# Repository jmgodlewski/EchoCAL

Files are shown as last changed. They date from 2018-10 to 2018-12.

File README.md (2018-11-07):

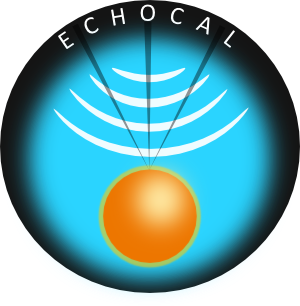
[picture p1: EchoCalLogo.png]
EchoCAL Logo
# EchoCAL: A Wireless Echosounder Calibration System. 

The EchoCAL Wireless Echosounder Calibration System was designed to give Ocean Acoustics researchers the ability to control motorized downriggers remotely during scientific echosounder calibrations. A typical downrigger station consists of a control box wired to a Canon downrigger which is mounted on the railing of the research vessel. A typical calibration on a research vessel requires at least three downrigger stations. (Two on one side of the vessel, and one on the other side.)

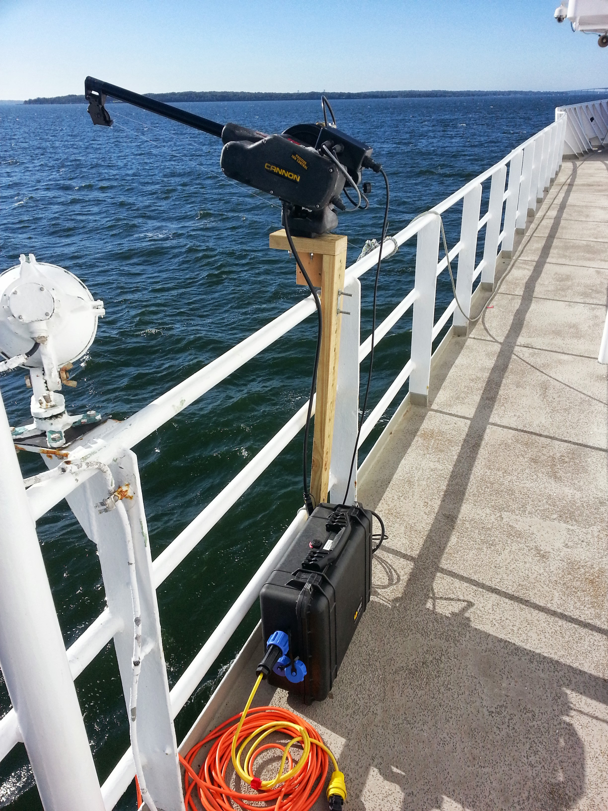
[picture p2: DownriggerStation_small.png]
Smaller Picture of Downrigger Station


The reseacher can control these downriggers wirelessly from inside the vessel. (See the figure below for a system diagram.)

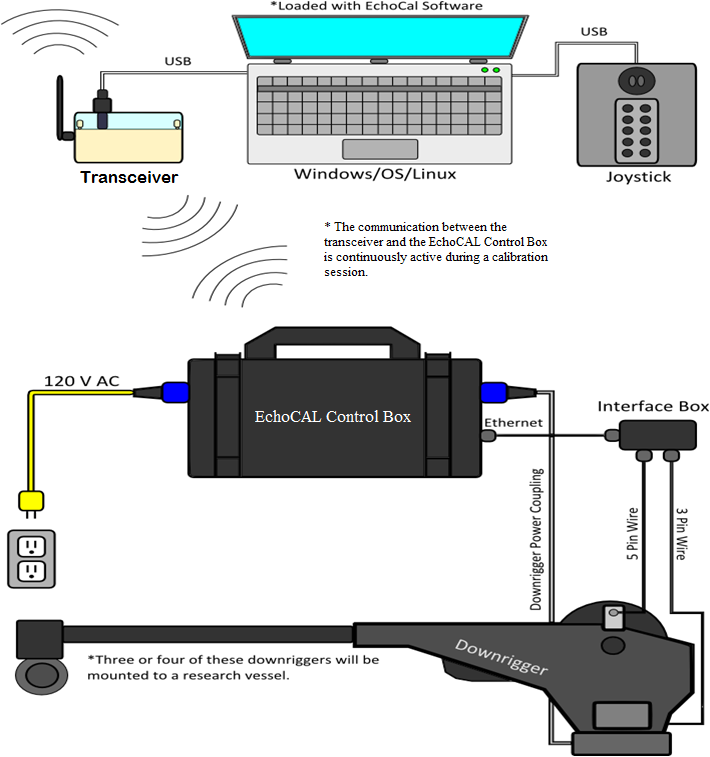
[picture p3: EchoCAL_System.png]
Diagram of EchoCAL System


## EchoCAL Project Files:

The following folders contain the required documentation to build one EchoCAL system:

### DesignFiles:

This folder contains a parts list as well as wiring diagrams for all EchoCAL hardware. This folder has two subfolders, "CircuitCard" and "WiringDiagrams". The "CircuitCard" folder contains the design files to manufacture the EchoCAL custom printed circuitboard (PCB). The "WiringDiagram" folder contains CAD, DXF, and PDF drawings for building all of the hardware for EchoCAL.

### Documentation:

This folder has the Software/Firmware Installation Manuals and the User Manuals.

### EchoCAL_GUI_Source:

This folder contains all of the [Netbeans](https://netbeans.org) JAVA Project source code for the EchoCAL Graphical User Interface (GUI).

### Parallax_Firmware:

This folder contains the firmware for the [Parallax Propeller](https://www.parallax.com/catalog/microcontrollers/propeller) Microcontroller.

### WGFAST_Presentation:

This folder contains a Microsoft PowerPoint presentation of the EchoCAL System. This presentation was given at the Working Group on Fisheries Acoustics, Science, and Technology ([WGFAST](http://www.ices.dk/community/groups/Pages/WGFAST.aspx)) meeting in May 2014. 

### bin:

This folder contains the executable code for the EchoCAL Graphical User Interface (GUI). The JAVA executable code is stored as a ZIP archive that can be downloaded and extracted on a user's computer. The archive was created using Netbeans IDE 8.1 and JAVA JDK 1.8 (64bit).

The "bin" folder has two subfolders, "Win64" and "Linux64". Download the proper version depending on which operating system you will be using.

## Designers:

* **Joseph Godlewski** - *Hardware/Firmware Design* - [jmgodlewski](https://github.com/jmgodlewski)

* **Michael Ryan**     - *EchoCAL GUI Design* - [spacetimeengineer](https://github.com/spacetimeengineer)

## License

EchoCAL is open source! See [LICENSE](./LICENSE.md) for complete license information.

The hardware/software design was written as beerware; if you see us at the local pub, and you've found the hardware and software helpful, please buy us a round!

Please use, reuse, and modify these files as you see fit. Please maintain attribution to NOAA Fisheries, Northeast Fisheries Science Center, and release anything derivative under the same license.

Distributed as-is; no warranty is given.

This project is licensed under the MIT License - see the [LICENSE.md](LICENSE.md) file for details.

## Acknowledgments:

* [Fizzed.com](http://fizzed.com/oss/rxtx-for-java) : Thanks to the developers at Fizzed.com for creating the open source 64-bit modules of the **RXTX** serial communication libraries for JAVA.

* [JInput](https://github.com/jinput/jinput) : Thanks to the developers and maintainers of the open source **JInput** JAVA module for interfacing USB Joystick controllers with Java applications.

* [Parallax Object Exchange](http://obex.parallax.com/) : Thanks to all of the developers who supplied numerous SPIN and Assembly code for the **Parallax Propeller** microcontroller. Their work has made the Propeller microcontroller a joy to work with.

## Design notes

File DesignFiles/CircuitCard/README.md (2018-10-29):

# EchoCAL: Custom Printed Circuit Board (PCB)

The EchoCAL Control Box includes a custom-built printed circuit board "PCB" which incorporates a [Parallax Microcontroller](https://www.parallax.com/product/p8x32a-d40) to interact with Canon Downriggers. This PCB also provides wireless communications with the controlling PC.

These boards can be purchased through [ExpressPCB.com](https://www.expresspcb.com/) using their free schematic and PCB design software.

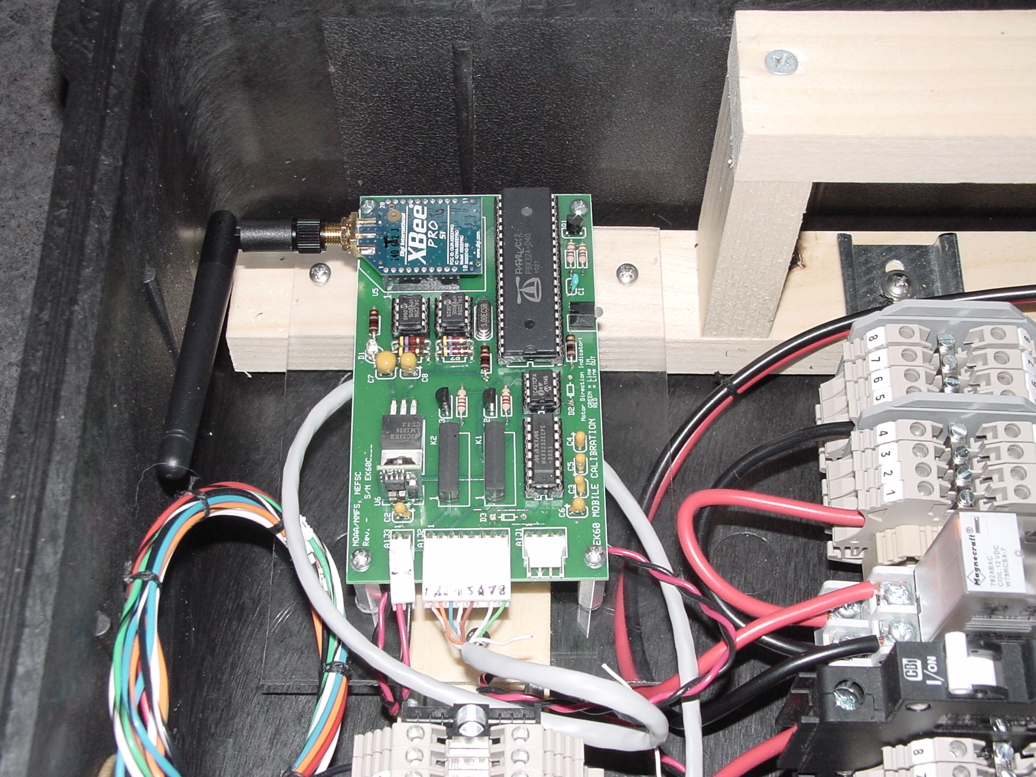
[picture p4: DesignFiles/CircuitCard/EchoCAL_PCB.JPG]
Picture Of PCB


## Purchasing Circuit Boards:

1. Open the "EchoCal_Wireless_RevB.pcb" file using the "expresspcbplus" application.

2. Select the "Order Boards" menu item and choose what type/quantity of boards that you would like. Note: Your PC must be connected to the internet before you can order circuit boards.

### Prerequisites:

The ExpressPCB software runs on Windows PCs only.

## Free Design Software from expresspcb.com

* [ExpressSCH](https://www.expresspcb.com/expresssch/) - Schematic Design software for "EchoCAL_Wireless_RevB.sch" file.
* [ExpressPCB Plus](https://www.expresspcb.com/expresspcbplus/) - PCB Design software for "EchoCAL_Wireless_RevB.pcb" file.

## Designer:

* **Joseph Godlewski** - *Hardware/Firmware Design* - [jmgodlewski](https://github.com/jmgodlewski)

## License

EchoCAL is open source! See [LICENSE](./LICENSE.md) for complete license information.

The hardware/software design was written as beerware; if you see me at the local pub, and you've found the hardware and software helpful, please buy me a round!

Please use, reuse, and modify these files as you see fit. Please maintain attribution to NOAA Fisheries, Northeast Fisheries Science Center, and release anything derivative under the same license.

Distributed as-is; no warranty is given.

This project is licensed under the MIT License - see the [LICENSE.md](LICENSE.md) file for details

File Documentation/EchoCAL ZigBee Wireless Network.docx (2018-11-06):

EchoCAL ZigBee Wireless Network:

Monitoring Network Signal Strength using DigiKey “XCTU” software.

1. A special software package developed by Digi International called “XCTU” is used to monitor the signal strength on the EchoCAL wireless network. This program allows the operator to visually see the signal strengths of all nodes in the ZigBee wireless mesh network.
2. Plug the EchoCAL Base Station into the PCs USB port. Verify which COM port is assigned to this base station using Window’s Device Manager.

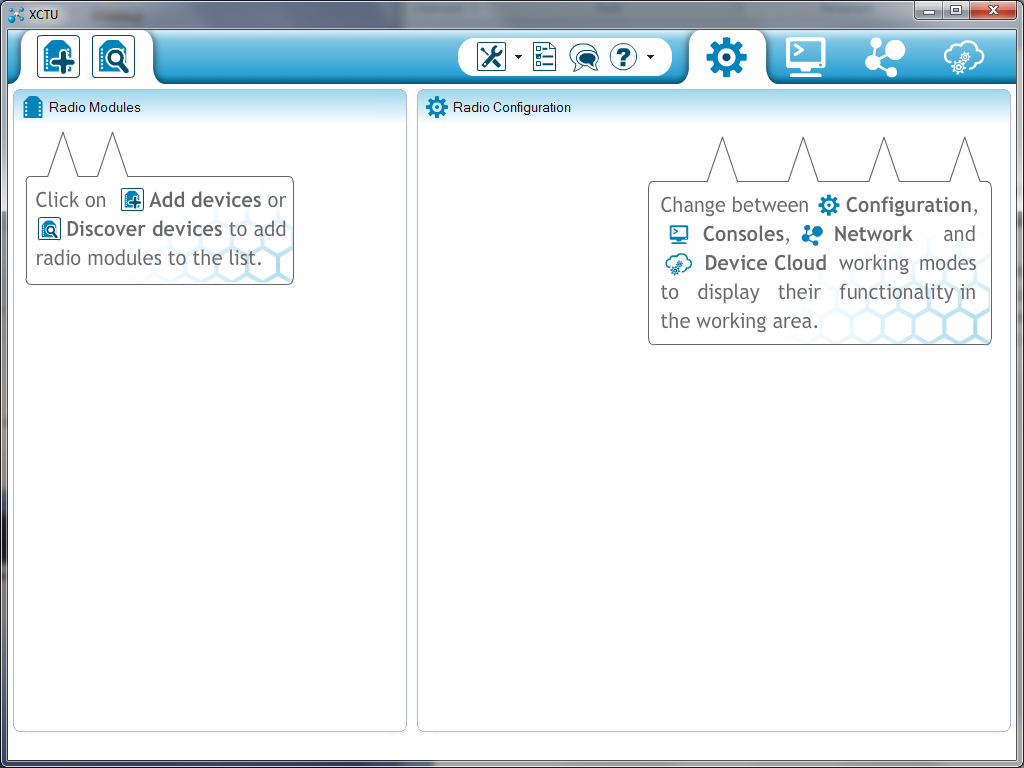
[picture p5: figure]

3. Launch the XCTU software by double-clicking the XCTU icon on the PCs desktop. The XCTU main window will open on the PC.

Discover Devices Tool

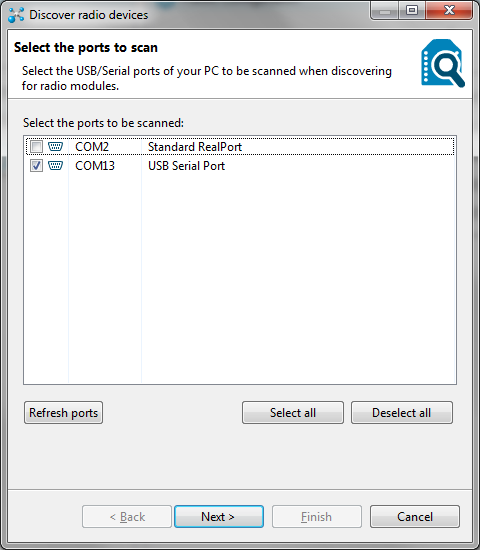
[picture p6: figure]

4. Click on the “Discover devices” tool icon on the top left portion of the XCTU window. This tool allows the software to automatically locate ZigBee transceivers attached to the PC. At this point, the “Discover radio devices” window will open. Select the checkbox next to the COM port that the EchoCAL Base Station is attached to. Click on the “Next” button at the bottom of the window to continue.
5. The “Set port parameters” window will open. Verify that the Serial/USB port parameters are properly configured:
- Baud Rate: 9600,
- Data Bits : 8,
- Parity: None,
- Stop Bits: 1,
- Flow Control: None.

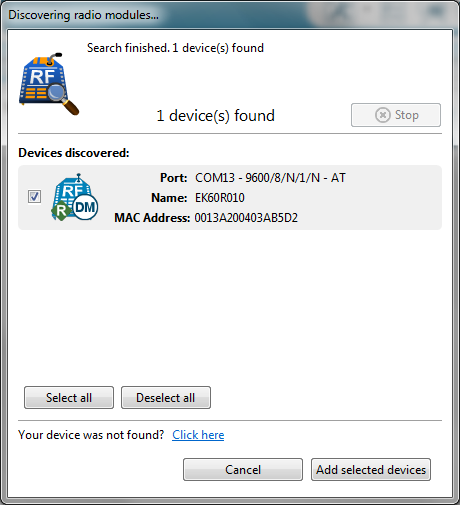
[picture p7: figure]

6. Click on the “Finish” button to continue. A new window will open which will show the device discovered on the PCs COM port. When the device appears on the “Devices discovered” portion of the window, verify that the correct device has been identified. Note: The devices name should be “EK60R010”. Once the device appears, select the “Add selected devices” button to select the base station transceiver.
7. The selected transceiver will appear in the main XCTU window in the left column. Click on this device, and the transceiver’s parameters will begin loading on the right side of window. Using the scroll bar on the right side of the window, scroll down the parameter list until you get to the “Serial Interfacing” portion of the transceiver’s parameter list. Locate the “AP API Enable” parameter under the Serial Interfacing section. In normal EchoCAL operation, this parameter should be set to “Transparent Mode [0]”. Click on this parameter to change the setting to “API without escapes [1]”. This parameter will turn GREEN, indicating that a change was made to this parameter. Click on the red “Pencil” icon to the right of this parameter to save it to the transceiver. Once the “Pencil” icon is selected, the change will be written to the transceiver, and the parameter will turn BLUE in the window. This change needs to be made to allow the transceiver to query other devices on the network about their configuration settings.

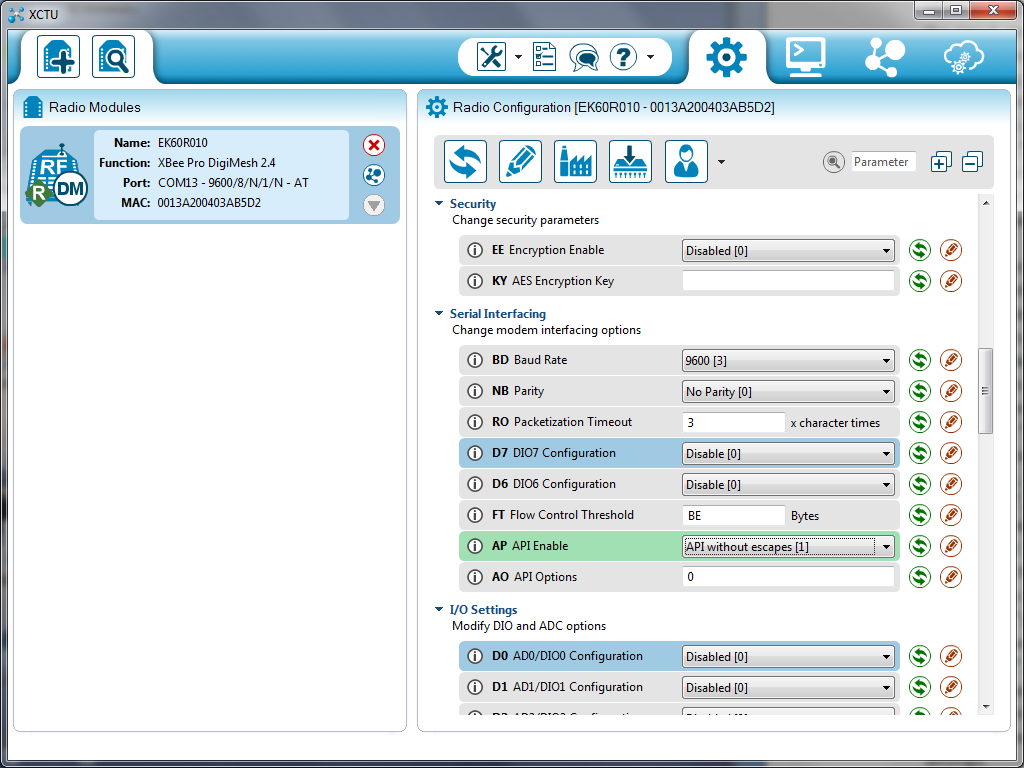
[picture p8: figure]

Discover radio nodes in same network icon:

8. Once the “AP API Enable” parameter has been changed, select the “Discover radio nodes in the same network” icon on the EK60R010 display on the left side of the main program window. This action will launch a new “Discovering remote devices” window, and the software will begin scanning the local wireless network for the various nodes that are available on the mesh network. Make sure all of the installed devices appear on the “New remote devices discovered” portion of this window. When all devices appear in this window, click on the “Add selected devices” button. This window will close, and the selected devices will appear below the base stations entry on the left column in the main XCTU window.

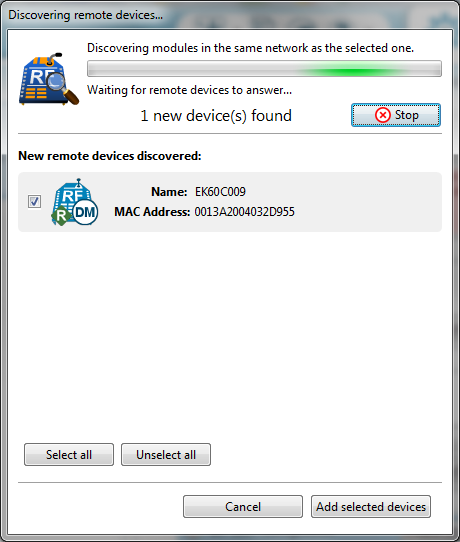
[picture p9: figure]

9. In the main XCTU window, select the “Switch to Networking Mode” tool icon on the right upper tool bar in the main window. The lower right portion will change to a tabbed interface showing the EK60R010 base station in the tab’s label.

Start/Stop scanning the radio module network.

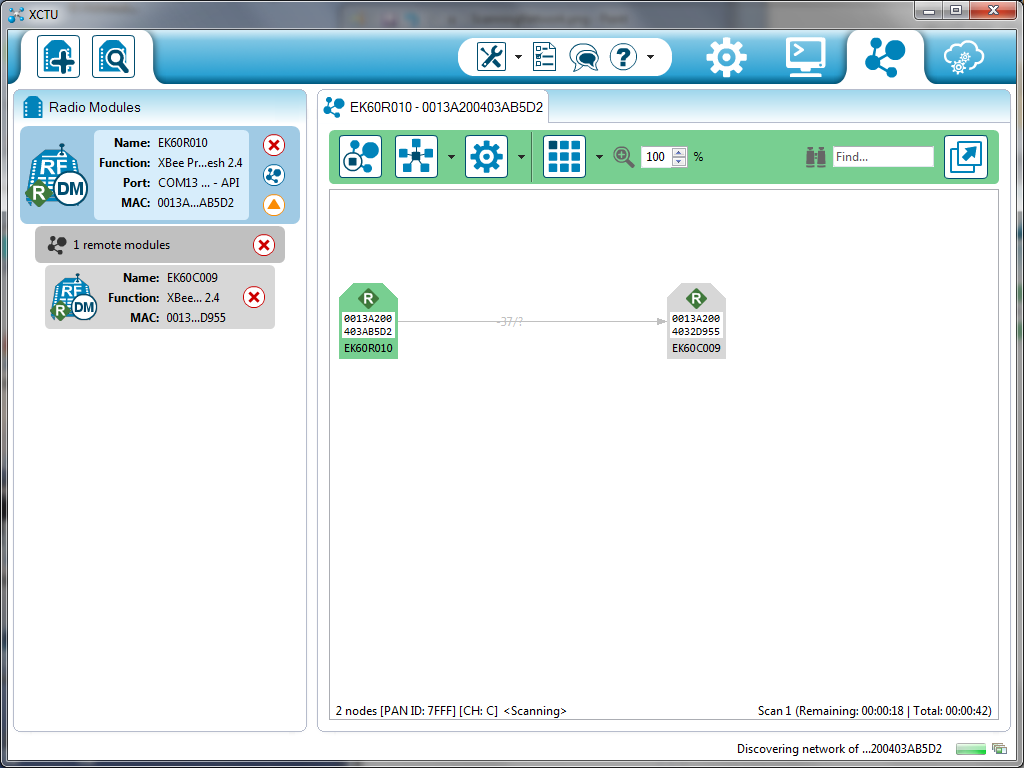
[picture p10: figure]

10. In the tab toolbar portion of the window, select the “Start scanning the radio module network” tool. The lower portion of the tab window will show the EK60R010 graphic which symbolizes the EchoCAL base station. All other transceivers on the network will begin appearing, with links between different transceivers that show the transmit/receive signal power levels. Verify that all of the transceivers appear, and that there is a sufficient transmission path between all transceivers in the network. When satisfied with the performance, select the “Stop scanning the radio module network” tool in the tab’s toolbar.
11. Select the “Switch to Configuration working mode” toolbar in the main window to bring up the parameter settings for the EK60R010 base station.
12. Using the scroll bar on the right side of the window, scroll down the parameter list until you get to the “Serial Interfacing” portion of the transceiver’s parameter list. Locate the “AP API Enable” parameter under the Serial Interfacing section. Click on this parameter to change the setting back to “Transparent Mode [0]”. This parameter will turn GREEN, indicating that a change was made to this parameter. Click on the red “Pencil” icon to the right of this parameter to save it to the transceiver. Once the “Pencil” icon is selected, the change will be written to the transceiver, and the parameter will turn BLUE in the window. This change needs to be made to allow the transceiver to query other devices on the network about their configuration settings.
13. Click on the red X icon on the base station graphic to close the COM port to the base station. Close the XCTU program.

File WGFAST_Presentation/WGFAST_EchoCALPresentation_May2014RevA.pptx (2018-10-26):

## EchoCAL: A mobile wireless calibration system for echo sounders.

Presented By:
Joseph M. Godlewski and Michael Ryan
NOAA,NMFS, NEFSC
Ecosystems Survey Branch
Advanced Sampling Technologies

## EchoCAL: A mobile wireless calibration system for echo sounders

- EchoCAL Hardware:
  - System Diagram;
  - Control Box Assembly;
  - Microcontroller Firmware;
  - Zigbee Wireless Protocol;
    - Wireless Base Station.
    - Wireless Routers.
- EchoCAL Software GUI.
- Results.

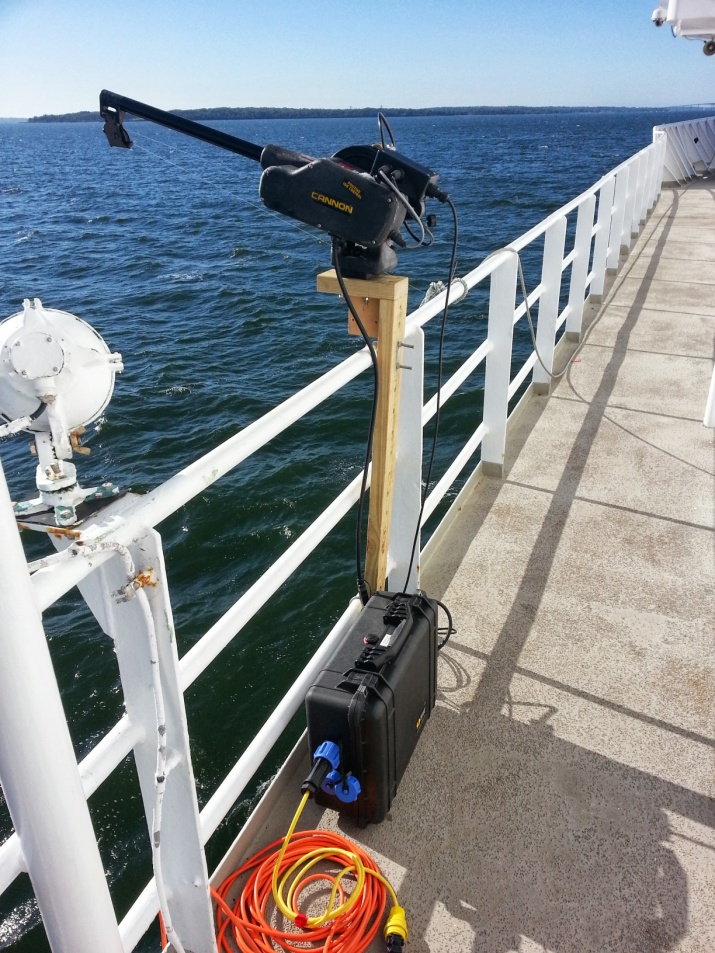
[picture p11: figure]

## EchoCAL System Diagram:

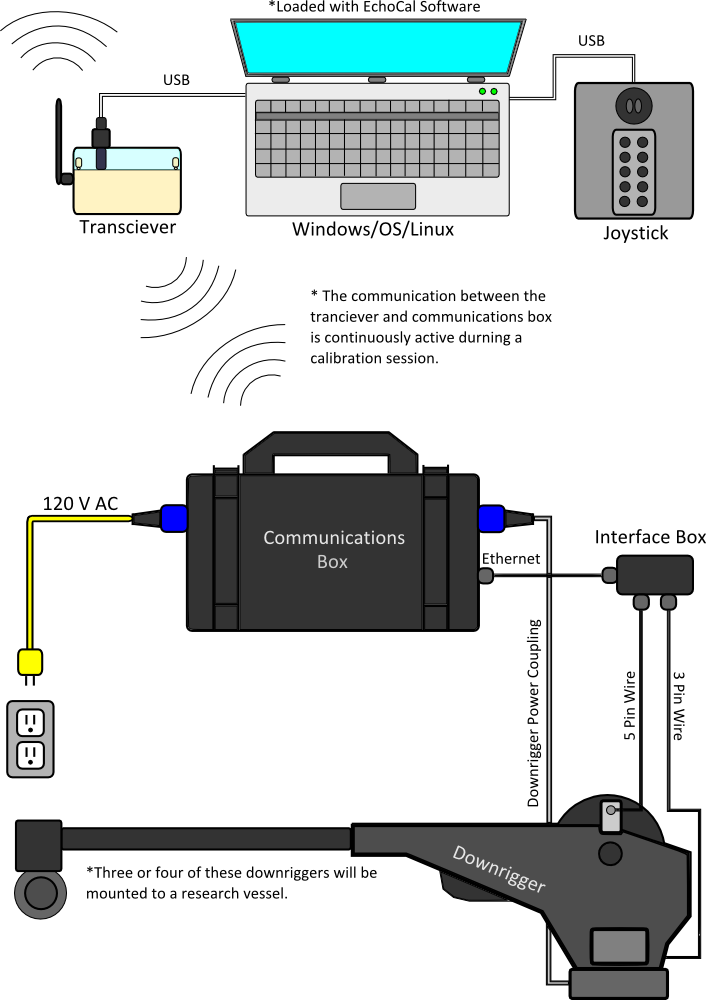
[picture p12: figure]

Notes: Modifications to Cannon Downrigger:

Added connector to downrigger case to wire control box relays in parallel with switch in downrigger.
Mounted 3PS Inc. Quadrature Encoder to outside of downrigger case.
Two magnets installed on downrigger wheel, each mounted at 180 degrees apart.
(This gives us approximately 6 inches of line movement with every “COUNT” of the encoder.)

## EchoCAL Control Box Assembly:

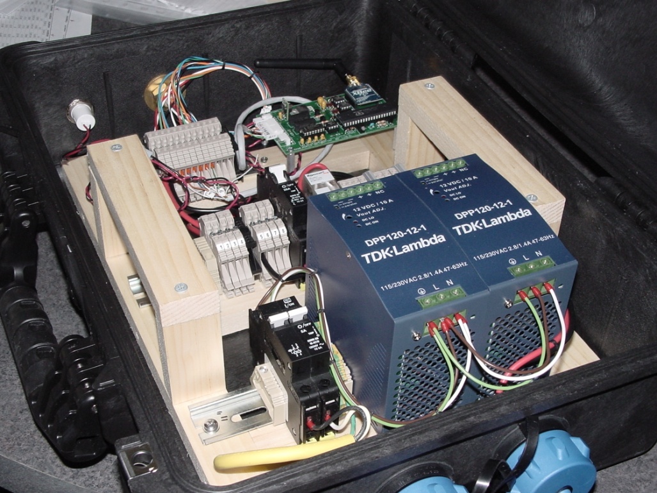
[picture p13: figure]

- Control Box consists of the following components:
  - Two TDK Lambda 12VDC, 10 Amp Power supplies;
  - One TDK Lambda 12VDC, 830 mA Power supply;
  - Custom circuit board with Parallax microcontroller and Digi International XBee Pro Wireless Transceiver;
  - Two power relays for switching between battery and AC power modes.

## Parallax Microcontroller Firmware:

- Parallax Microcontroller programmed using two languages designed specifically for it:
  - “Spin” language = High-level object-based,
  - “Propeller Assembly” = Low-level, highly optimized.
- Microcontroller has eight processing cores (Cogs) which act as a hardware threading mechanism. Allows functions to run in parallel. EchoCAL firmware uses three processing Cogs:
  - One Cog for Main program.
  - Second Cog for handling data and command I/O with XBee Pro transceiver.
  - Third Cog for monitoring the Encoder output and determining direction and line length (ie. Counts) that the downrigger has accomplished.

## XBee Pro Base Station and Router:

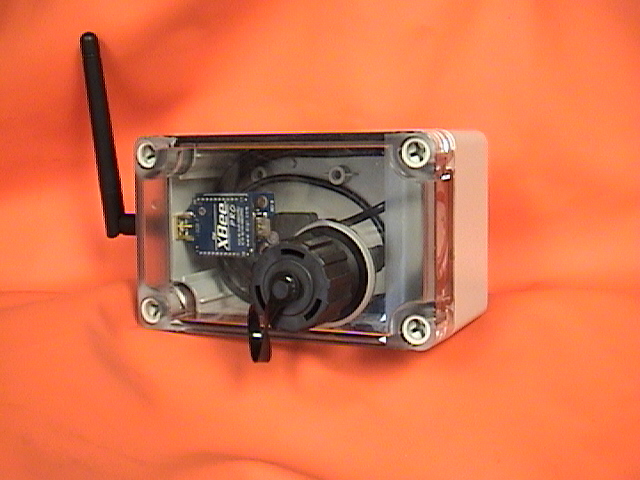
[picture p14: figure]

- The XBee Pro Base Station consists of the following:
  - Parallax XBee USB Adapter board;
  - One Digi Inc. XBee Pro Wireless Transceiver;
  - Power provided by USB bus in the PC.
- The XBee Pro Router hardware:
  - Powered by a 12 VDC, 2000 mAh battery pack.
  - Custom PCB which converts 12 VDC to 3.6 VDC for XBee Pro transceiver operation.

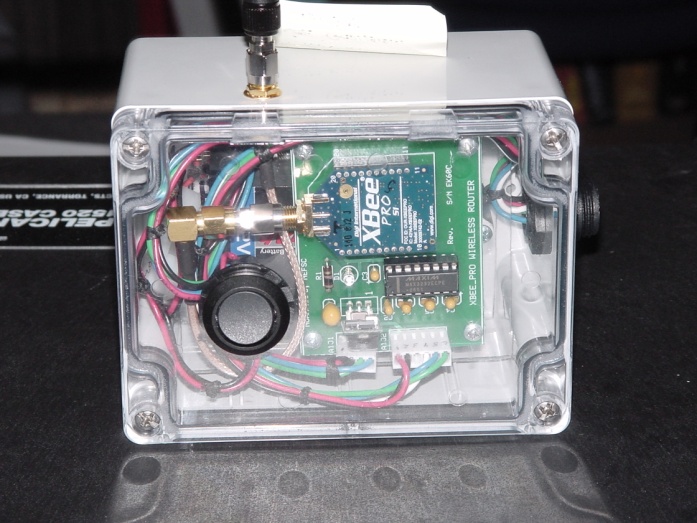
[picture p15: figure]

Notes: XBee Pro Base Station:
- Parallax XBee USB adapter board eliminates the need to build a custom circuit board.
- Simply mount XBee Pro transceiver to adapter board and you are in business.
- Power provided through the USB bus.

XBee Pro Router:
- Powered by a 12 VDC 2000 mAh battery pack.
- Custom circuit board that converts 12 VDC to 3.6 VDC for use with the XBee Pro transceiver.
- Board also contains an Analog Devices ADM3202 RS232 transceiver chip to provide RS232 support for upgrading the XBee Pro transceiver.
- We can do away with the custom PCB if we use the same Parallax XBee USB adapter board that was used in the Base Station.

## XBee Pro Digimesh Network:

- The XBee Pro network is known as a Low Rate Wireless Personal Area Network (LR-WPAN), commonly referred to as a Wireless Sensor Network:
  - Incorporates an Ad Hoc On-Demand Distance Vector mesh routing;
  - Self-healing and discovery capable for network stability;
  - Operates in the 2.4 GHz wireless frequency band;

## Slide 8

EchoCAL Software Interface:

- EchoCAL Software:
  - Developed using JAVA NetBeans IDE platform;
  - Joystick enabled;
  - Location indicators;
  - Programmatic sensors,
  - Hardware safety functions,
  - Automatic navigation function,
  - Navigate function (Sphere locator function).

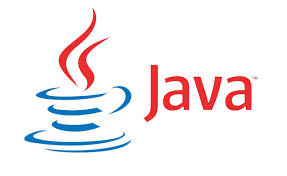
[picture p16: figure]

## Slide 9

EchoCAL Geometry Manager Inputs:
(Visual Reference)

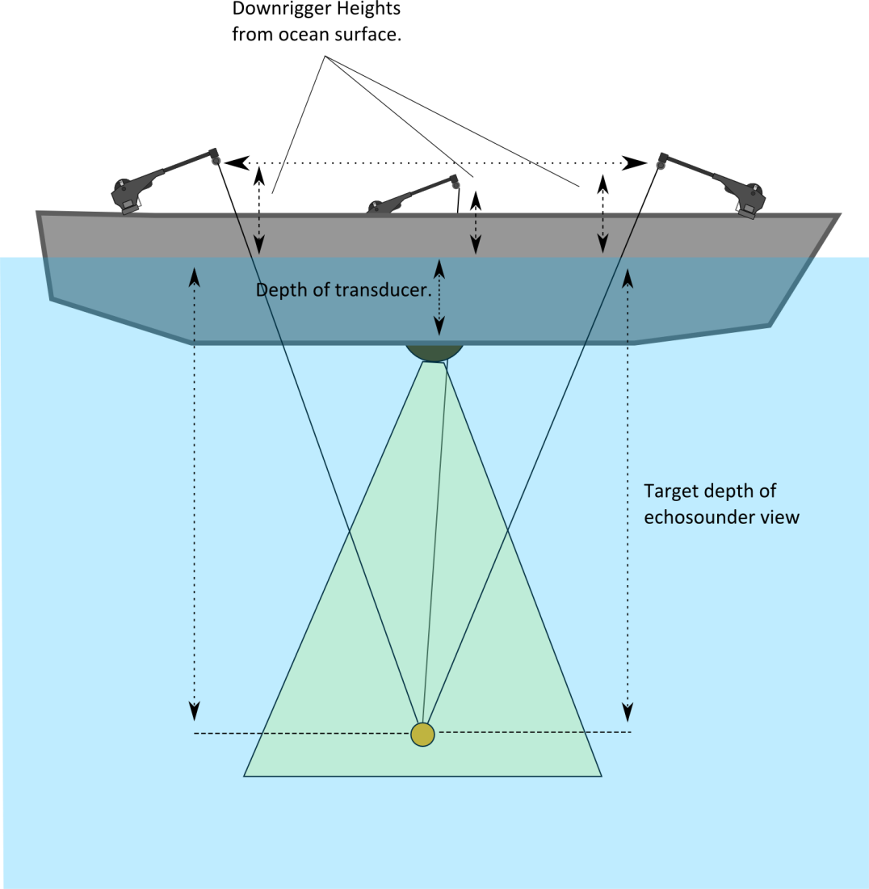
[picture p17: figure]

- Measurements are used to build a geometrical reference map which allows the EchoCAL system to perform accurate automated calibration sessions.

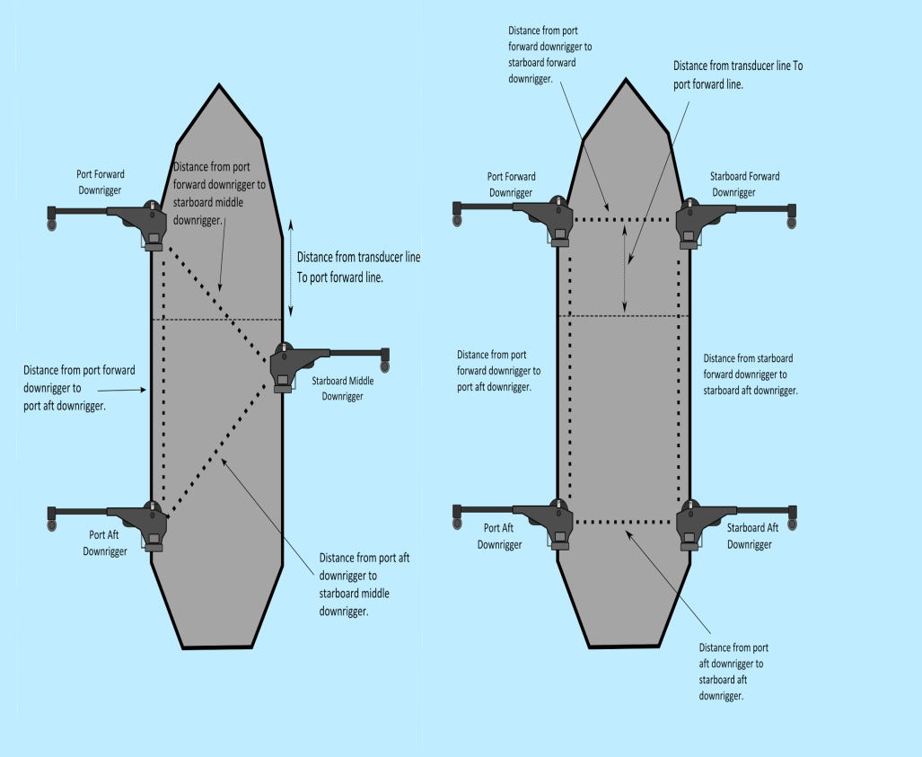
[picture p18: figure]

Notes: Vessel Config file is used to provide a general location of the mounted downriggers on the vessel.
Vessel specific measurements are made to determine the location of the downriggers with respect to the onboard echosounder transducers.

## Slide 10

EchoCAL Graphical User Interface:

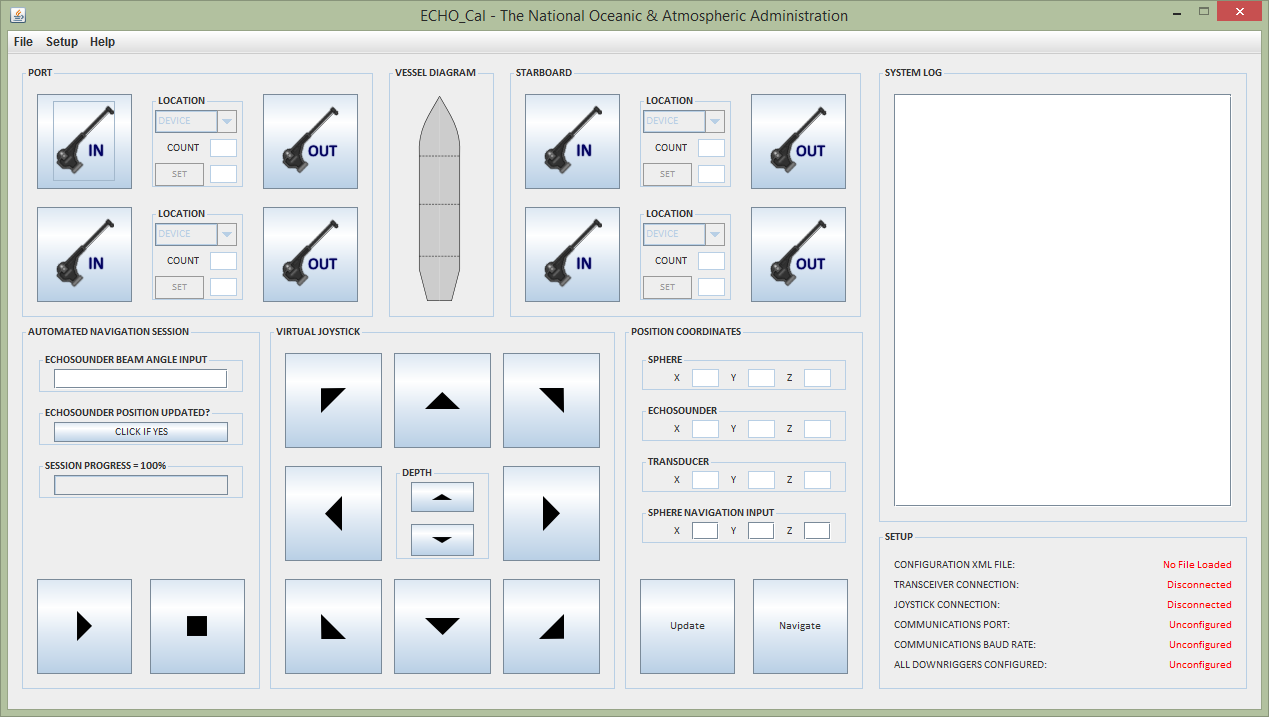
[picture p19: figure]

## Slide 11

EchoCAL’s True Power:
Coordinate Transformation Algorithms

- EchoCAL Software Coordinate Solutions:
  - Uses a process of coordinate filtering to find the Euclidian position of the calibration sphere.
  - Runs on a separate thread so that the geometrical information is updated in real time.
  - Uses the XML configuration file for a geometrical basis.
  - All inputs and outputs are Euclidian, but all calculations are done in downrigger coordinates.

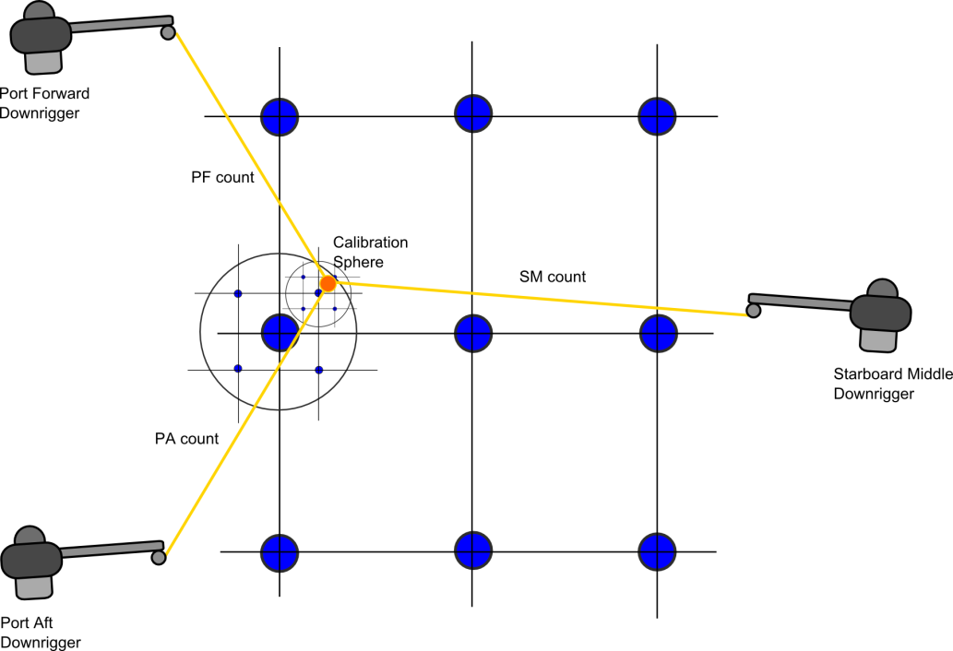
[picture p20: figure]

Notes: Graphic represents a two dimensional view of a three dimensional space.
Each circle represents a set of coordinates. The software checks which downrigger coord transformation is closest to the systems current downrigger counts, and builds another set of points around it. This method builds an array of coordinates

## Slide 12

EchoCAL Automated Calibration Session:

- EchoCALs Automated Navigation Function:
  - Automatically moves the sphere through echosounder beam in a “Star” shaped pattern.
  - Area covered is slightly larger than the beam angle that was input in the GUI.
  - Reasonable coverage is obtained in the echosounder beam.
  - An automated session takes approximately 10 minutes to perform, depending on beam angle size.

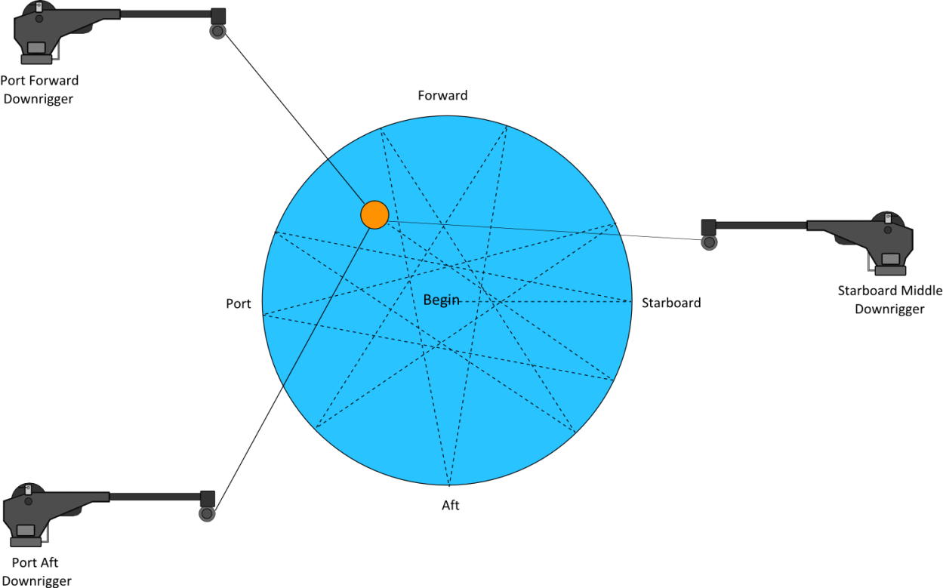
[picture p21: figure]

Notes: EchoCALs Automated Navigation Function:
Automatically moves the sphere through the echosounder beam in a “Star-shaped” pattern.
- Other patterns are being researched.
The area covered is slightly larger than the beam angle that was input in the GUI.
Reasonable coverage is obtained in the echosounder beam.
An automated session takes approximately 10 minutes to perform, depending on the beam angle size.

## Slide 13

EchoCAL Automated Calibration Session:

- EchoCALs Time Saving Abilities:
  - Initially locating the sphere in the echosounder beam can be a difficult task. (Especially when surface winds, or ocean currents are high.) Use of both the “Navigation” and “Auto-navigation” functions allow the operator to easily position the sphere in the echosounder’s beam.
  - Echosounder position updates; (Allows higher order corrections to geometry if system generated values are wrong).
  - Automated calibration sessions: Enjoy a coffee rather than standing out in the rain!

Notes: Time Saving Abilities:
- Initially finding the sphere in the echosounder beam can be a difficult task. (Especially when surface winds, or ocean currents are high.)
The “Navigation” and “Auto-navigation” functions of the EchoCAL software allow the operator to easily position the sphere in the echosounder’s
beam. The Navigation function will get the sphere to the proper depth, and in the vicinity of the echosounder’s beam. If the sphere is not seen
at this point, the operator can perform an initial “Auto-navigation” session with a larger than normal beam angle, and once the sphere appears
in the beam, the operator can stop the “Auto-navigation” session, and position the sphere using the joystick controls.
- Software allows the operator to update the position of the sphere in the center of a beam. This allows operator to reposition the sphere automatically in
the beam should the sphere somehow get lost during calibrations.

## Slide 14

Hardware Safety Functions:

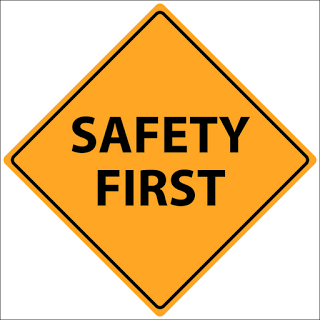
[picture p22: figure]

- EchoCAL Hardware Safety Functions:
  - Built-in tension sensor function to keep lines from breaking.
  - Built-in communication loss warning message.
  - Automatic system halting functions. (Pauses system when mechanical or communication failures occur).
  - Built-In real-time System Log for general information and system status.

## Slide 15

EchoCAL System Results:

- The EchoCAL echosounder calibration system has been used successfully on three NOAA vessels to date:
  - NOAA Ship Okeanos Explorer (April 2013),
  - NOAA Ship Gordon Gunter (April 2014),
  - NOAA Ship Henry Bigelow (September 2013, April 2014).
- Extending the wireless signal outside the vessels proved to be easier than expected. (Only three routers required for the above vessels.)

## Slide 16

EchoCAL System Results:

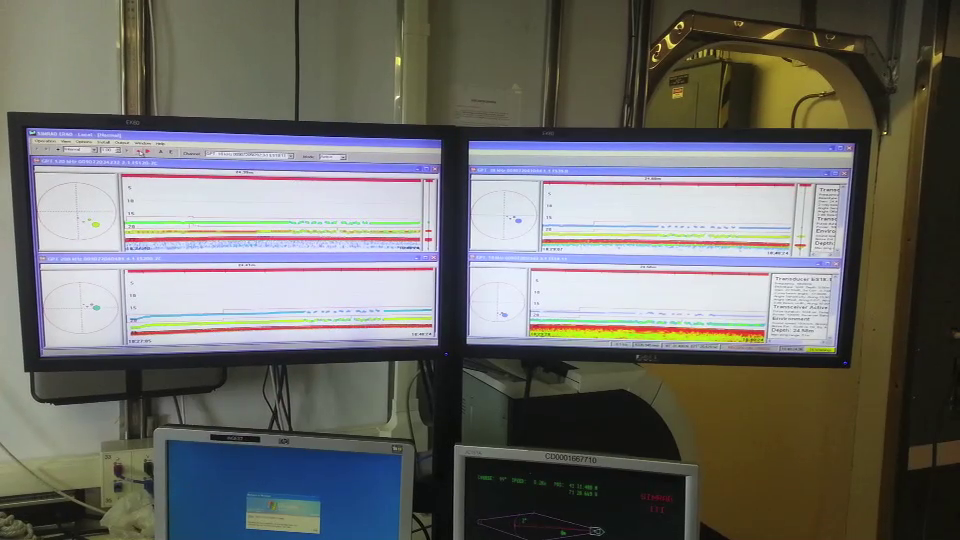
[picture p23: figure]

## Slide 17

EchoCAL System Results:

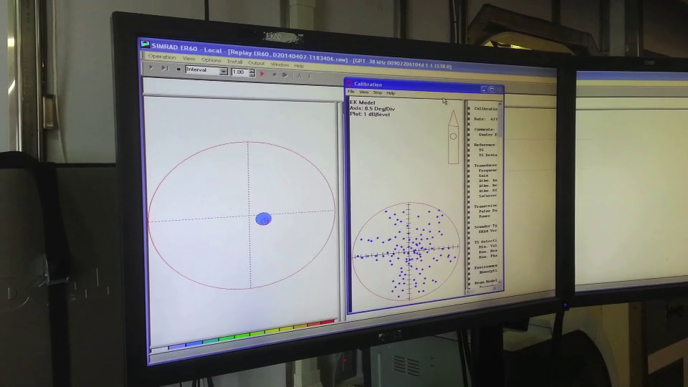
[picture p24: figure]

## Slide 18

- Questions?

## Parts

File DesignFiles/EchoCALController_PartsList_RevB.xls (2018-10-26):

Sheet: EchoCAL Control Box
EchoCAL Wireless Controller: Parts List
Part ID | Part Type | Description | Qty | Cost | Total | Source P/N | Part Source | Notes
EchoCAL Circuit Board A1 Parts:
A1 |  | EchoCAL Circuit Card (PCB) | 1 | $67.28 | $67.28 |  | Express PCB | Production Service (Qty=4) = $269.11.. (Qty = 10, $308.50)
A1J1 |  | Molex P/N 22-05-3041, 4-pin, RA, Friction-Lock Header | 1 | $0.49 | $0.49 | WM4302-ND | Digikey | RS-232 Input Header (4-Pin)
A1J2 |  | Molex P/N 22-05-3081, 8-pin, RA, Friction-Lock Header | 1 | $0.83 | $0.83 | WM4306-ND | Digikey | Downrigger Interface Header (8-Pin)
A1J3 |  | Molex P/N 22-05-3021, 2-pin, RA, Friction-Lock Header | 1 | $0.32 | $0.32 | WM4300-ND | Digikey | Power Input Header (2-Pin)
A1P1 |  | Molex P/N 22-01-3047, 4-socket, Terminal Housing | 1 | $0.19 | $0.19 | WM2002-ND | Digikey | RS-232 Input Connector (4-Socket)
A1P2 |  | Molex P/N 22-01-3087, 8-socket, Terminal Housing | 1 | $0.37 | $0.37 | WM2006-ND | Digikey | Downrigger Interface Connector (8-Socket)
A1P3 |  | Molex P/N 22-01-2027, 2-socket, Terminal Housing | 1 | $0.10 | $0.10 | WM2011-ND | Digikey | Power Input Connector (2-Socket)
 |  | Molex P/N 08-50-0114, Crimp Terminals | 100 | $0.10 | $10.00 | WM1114-ND | Digikey | Crimp sockets for connectors above.
C1 | 0.01uF | Ceramic, +/- 10% | 1 | $0.32 | $0.32 | 490-8813-ND | Digikey
C2 | 1uF | Tantalum, +/- 10% | 1 | $0.65 | $0.65 | 478-1835-ND | Digikey
C3 | 0.1uF | Tantalum, +/- 10% | 1 | $0.66 | $0.66 | 478-1831-ND | Digikey
C4 | 0.1uF | Tantalum, +/- 10% | 1 | $0.46 | $0.46 | 478-1831-ND | Digikey
C5 | 0.1uF | Tantalum, +/- 10% | 1 | $0.46 | $0.46 | 478-1831-ND | Digikey
C6 | 0.1uF | Tantalum, +/- 10% | 1 | $0.46 | $0.46 | 478-1831-ND | Digikey
C7 | 100uF | Tantalum, +/- 10% | 1 | $2.64 | $2.64 | 478-1844-ND | Digikey
C8 | 10uF | Tantalum, +/- 10% | 1 | $0.94 | $0.94 | 478-1841-ND | Digikey
C9 | 1uF | Tantalum, +/- 10% | 1 | $0.65 | $0.65 | 478-1835-ND | Digikey
C10 | 8.2 pF | Ceramic, +/- 5% | 1 | $0.51 | $0.51 | 399-8923-ND | Digikey
D1 |  | Red LED, radial, 3 mm, T-1 | 1 | $0.68 | $0.68 | 511-1190-ND | Digikey
K1 - K2 | W117SIP-6 Relay | Schneider Electric W117SIP-6 Reed Relay, SPST-NO, 5 VDC, 0.5A | 2 | $4.34 | $8.68 | 10M6260 | Newark | www.newark.com (http://www.newark.com/schneider-electric-magnecraft/w117sip-6/relay-reed-spst-no-200v-0-5a-tht/dp/10M6260?ost=10M6260&ddkey=http%3Aen-US%2FElement14_US%2Fsearch)
R1 | 10K | 0.25 W, carbon film resistor, +/- 5% | 1 | $0.10 | $0.10 | 10KQBK-ND | Digikey
R2 | 10K | 0.25 W, carbon film resistor, +/- 5% | 1 | $0.10 | $0.10 | 10KQBK-ND | Digikey
R3 | 10K | 0.25 W, carbon film resistor, +/- 5% | 1 | $0.10 | $0.10 | 10KQBK-ND | Digikey
R4 | 4.7K | 0.25 W, carbon composite resistor, +/- 5% | 1 | $0.10 | $0.10 | CF14JT4K70 | Digikey
R5 | 4.7K | 0.25 W, carbon composite resistor, +/- 5% | 1 | $0.10 | $0.10 | CF14JT4K70 | Digikey
R6 | 4.7K | 0.25 W, carbon composite resistor, +/- 5% | 1 | $0.10 | $0.10 | CF14JT4K70 | Digikey
R7 | 4.7K | 0.25 W, carbon composite resistor, +/- 5% | 1 | $0.10 | $0.10 | CF14JT4K70 | Digikey
R8 | 100 | 0.25 W, carbon composite resistor, +/- 5% | 1 | $0.10 | $0.10 | CF14JT100RCT-ND | Digikey
R9 | 200 | 0.25 W, carbon film resistor, +/- 5% | 1 | $0.10 | $0.10 | 200QBK-ND | Digikey
R10 | 200 | 0.25 W, carbon film resistor, +/- 5% | 1 | $0.10 | $0.10 | 200QBK-ND | Digikey
R11 | 100 | 0.25 W, carbon composite resistor, +/- 5% | 1 | $0.10 | $0.10 | CF14JT100RCT-ND | Digikey
R12 | 20K | 0.25 W, carbon composite resistor, +/- 5% | 1 | $0.10 | $0.10 | 20KQBK-ND | Digikey
R13 | 20K | 0.25 W, carbon composite resistor, +/- 5% | 1 | $0.10 | $0.10 | 20KQBK-ND | Digikey
LT1 |  | Dialight LED Indicator, 3 mm, RED/GREEN, 2.1 Vdc | 1 | $1.76 | $1.76 | 30K1707 | Newark | www.newark.com (http://www.newark.com/dialight/551-3007f/indicator-led-pcb-3mm-red-green/dp/30K1707?ost=30K1707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)
U1 | P8X32A-D40 | Parallax Propeller Microcontroller | 1 | $7.99 | $7.99 | P8X32A-D40-ND | Digikey
U2 | ADM3202ANZ | Analog Divices ADM3202ANZ RS232 Transceiver 460KBPS3.3V DIP16 | 1 | $3.02 | $3.02 | ADM3202ANZ-ND | Digikey
U3 | 24LC256 | 24LC256-E/P 256K EEPROM by MICROCHIP | 1 | $0.91 | $0.91 | 24LC256-E/P-ND | Digikey | I indicates Temp range -45 to 85 C. E = -45 to 125 C.
U4 | 24LC256 | 24LC256-E/P 256K EEPROM by MICROCHIP | 1 | $0.91 | $0.91 | 24LC256-E/P-ND | Digikey | I indicates Temp range -45 to 85 C. E = -45 to 125 C.
U5 | XBee_Pro | Digi Xbee_Pro Wireless Transceiver, XBP9B-DMST-002 | 1 | $39.00 | $39.00 | 602-1299-ND | Digikey | www.digikey.com (https://www.digikey.com/products/en?keywords=602-1299-ND)
 | Antenna | Antenna - 900 MHz, HG, RPSMA Male, articulating | 1 | $7.63 | $7.63 | 553-1474-ND | Digikey | www.digikey.com (https://www.digikey.com/products/en?keywords=553-1474-nd)
U6 | OKI-78SR-5/1.5W36C | Murata OKI-78SR-5 DC to DC Converter, 7.5 W, 5 Vdc output | 1 | $4.30 | $4.30 | 811-2196-5-ND | Digikey
U7 | LM1086IT-3.3/NOPB | LM1086IT-3.3-NOPB by National Semiconductor | 1 | $1.86 | $1.86 | LM1086IT-3.3/NOPB-ND | Digikey
U8 | TC427CPA | Microchip TC427CPA MOSFET Driver, Low Side, 8-pin DIP | 1 | $1.36 | $1.36 | TC427CPA-ND | Digikey | MOSFET Driver
Q1 - Q3 | 2N3904BU | 2N3904 Bipolar Transistor NPN, ON Semiconductor | 3 | $0.21 | $0.63 | 2N3904FS-ND | Digikey
X1 | 5MHz | ECS-50-20-4 5.0 MHz Crystal Oscillator by ECS | 1 | $0.69 | $0.69 | X410-ND | Digikey | This is a 5.0000 MHz crystal
 | A 08-LC-TT | DIP Socket, 8-Pin, AssmanN P/N A08-LC-TT | 3 | $0.18 | $0.54 | AE9986-ND | Digikey
 | A 16-LC-TT | DIP Socket, 16-Pin, AssmanN P/N A16-LC-TT | 1 | $0.25 | $0.25 | AE9992-ND | Digikey
 | A 40-LC-TT | DIP Socket, 40-Pin, AssmanN P/N A40-LC-TT | 1 | $0.51 | $0.51 | AE10008-ND | Digikey
 | SQT-110-01-L-S | SIP Socket, 10-Pin, Samtec P/N SQT-110-01-L-S, 2.00 mm Pitch | 2 | $4.03 | $8.06 | SAM1247-10-ND | Digikey
EchoCAL Control Box Case Parts:
CB1 | C5A2P-489 | American Electrical Circuit Breaker, 240 VAC 5 Amp, 2-pole | 1 | $34.02 | $34.02 | 288-1363-ND | Digikey
CB2 | C20A1P-80VDC | American Electrical Circuit Breaker, 80 VDC 20 Amp, single pole | 1 | $21.06 | $21.06 | 288-1373-ND | Digikey
TB1,2,3 | PEK 2.5 | American Electric Terminal Block, Series PEK 2.5K | 100 | $1.14 | $114.00 | 288-1240-ND | Digikey
 | UK2.5/4 | American Electric Terminal Block Jumpers, 4 Pos. | 15 | $2.39 | $35.85 | 288-1269-ND | Digikey
 | NPP 2.5-10 | American Electric Terminal Block End Plate | 100 | $0.32 | $32.00 | 288-1259-ND | Digikey
 | ASK | American Electric End Bracket | 50 | $0.36 | $18.00 | 288-1295-ND | Digikey
 | 505020 | AE Marking Tags, DY5 | 1 | $1.72 | $1.72 | 288-1296-ND | Digikey
 | 331120 | AE Ground Block, WGT 2.5 | 3 | $3.23 | $9.69 | 288-1248-ND | Digikey
PS1 & 2 | DPP120-12-1 | TDK Lambda 12 VDC Power Supply, 10 Amp | 2 | $80.80 | $161.60 | 285-2032-ND | Digikey
PS3 | DSP10-12 | TDK Lambda 12 VDC Power Supply, 0.830 Amp | 1 | $24.44 | $24.44 | 285-1225-ND | Digikey
K1 | XT484LB2 | Tyco/Schrack Interface Plug-In Relay, 12 VDC coil, 360 ohm | 1 | $8.33 | $8.33 | PB1196-ND | Digikey
 | 6-1415035-1 | Screw terminal, DIN Rail Socket for relay K1 | 1 | $4.95 | $4.95 | PB780-ND | Digikey
K2 | 782XBXC-12D | Magnecraft Power Relay, 12 VDC coil, 20 Amp rated contacts | 1 | $10.54 | $10.54 | 528-7880-7 | Mouser | www.mouser.com
 | 70-459-1 | DIN Rail Socket for relay K2 | 1 | $7.45 | $7.45 | 528-459 | Mouser | www.mouser.com
J1 | PX0931 | Bulgin Bucaneer 900 Series Receptacle, P/N PX0931/03/P | 1 | $23.37 | $23.37 | 708-1205-ND | Digikey | www.digikey.com
P1 | PX0911 | Bulgin Bucaneer 900 Series Plug, P/N PX0911/03/S | 1 | $31.95 | $31.95 | 708-1190-ND | Digikey | www.digikey.com
J2 | PX0931 | Bulgin Bucaneer 900 Series Receptacle, P/N PX0931/02/P | 1 | $19.82 | $19.82 | 708-1204-ND | Digikey | www.digikey.com
P2 | PX0911 | Bulgin Bucaneer 900 Series Plug, P/N PX0911/02/S | 1 | $23.64 | $23.64 | 708-1189-ND | Digikey | www.digikey.com
J3 | PX0931 | Bulgin Bucaneer 900 Series Receptacle, P/N PX0931/02/S | 1 | $21.68 | $21.68 | 708-1209-ND | Digikey | www.digikey.com
P3 | PX0911 | Bulgin Bucaneer 900 Series Plug, P/N PX0911/02/P | 1 | $26.78 | $26.78 | 708-1184-ND | Digikey | www.digikey.com
 | PX0970 | Plastic Cap for J1,J2, & J3 | 3 | $7.94 | $23.82 | 708-1226-ND | Digikey | www.digikey.com
 | 2UB3001-W0000W | Plastic Cap for J1, MultiComp | 1 | $1.97 | $1.97 | 20T7280 | Newark | www.newark.com
J4 | 2TJ3003-W05100 | MultiComp P/N 2TJ3003-W05100, RJ45 Jack, 8 Pos, Panel | 1 | $9.30 | $9.30 | 20T7279 | Newark | www.newark.com
 | 2TJ3000-W05103 | MultiComp Computer Cable, RJ45, 3.5 Meter Length, Black | 1 | $23.77 | $23.77 | 20T7277 | Newark | Use for cable assembly EchoCAL-10520
L1 | 557-1103-203F | Dialight 557 Series Watertight LED Indicator, Red, 12 VDC | 1 | $14.19 | $14.19 | 33M4324 | Newark | www.newark.com
Case | 1520 | Pelican Case, P/N 1520 | 1 | $113.53 | $113.53 |  | Pelican | www.thepelicanstore.com
 | DIN Rail | DIN Rail, 35 x 7.5mm, Slotted 36 inch | 2 | $3.70 | $7.40 | ADR3575-S3600-ND | Digikey | www.digikey.com
 |  |  | TOTAL: |  | $1002.28
 |  | Control Box Total: | $1002.28
 |  | XBeePro Router Total: | $167.24 | Price is for one router. You probably need about three routers to get wireless signal outside research vessel.
 |  | Downrigger Interface Box Total: | $83.65
 |  | Wireless Base Station: | $126.81
 |  | 3PS Inc. Hall Effect Sensor P/N QUAD101-01-01-01-0 | $850.80 | Need to reconsider use of this sensor. Price has almost tripled in the past 5 years.
 |  | Cannon Magnum 5ST Downrigger: | $429.99
 |  | Total System Cost per unit: | $2660.77

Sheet: XBeePro Router
XBee_Pro Wireless Router: Parts List
Part ID | Part Type | Description | Qty | Cost | Total | Source P/N | Part Source | Notes
XBee_Pro Router Circuit Board A1 Parts:
A1 |  | Sparkfun XBee Explorer, P/N WRL-11373 | 1 | $9.95 | $9.95 | WRL-11373 | Sparkfun | Sparkfun.com (https://www.sparkfun.com/products/11373)
A1J1 |  | Molex P/N 22-05-3081, 6-pin, RA, Friction-Lock Header | 1 | $0.65 | $0.65 | WM4304-ND | Digikey | Power/XBee Interface Right Angle Header (6-Pin)
A1P1 |  | Molex P/N 22-01-2067, 6-socket, Terminal Housing | 1 | $0.26 | $0.26 | WM2015-ND | Digikey | Power/XBee Interface Connector (6-Socket)
 |  | Molex P/N 08-50-0114, Crimp Terminals | 100 | $0.10 | $10.00 | WM1114-ND | Digikey | Crimp sockets for connectors above.
U3 | XBee_Pro | Digi Xbee_Pro Wireless Transceiver, XBP9B-DMST-002 | 1 | $39.00 | $39.00 | 602-1299-ND | Digikey | www.digikey.com (https://www.digikey.com/products/en?keywords=602-1299-nd)
 | Antenna, 900 MHz | Antenna - 900 MHz, Half Wave Dipole, 2.1 dBi, RPSMA Male, articulating | 1 | $7.63 | $7.63 | 553-1474-ND | Digikey | www.digikey.com (https://www.digikey.com/products/en?keywords=553-1474-nd)
XBee Router Case Parts:
B1 | 4.8 VDC Battery | Tenergy 4.8 V 2000 mAh NiMH Battery Pack | 1 | $12.99 | $12.99 | 11001 | All-Battery.com | www.all-battery.com (http://www.all-battery.com/48v2000mahnimhreceiverrxbattery11001.aspx)
S1 | Power Switch | E-Switch P/N RR313BBLKBLKES, Rocker Switch | 1 | $3.45 | $3.45 | 612-RR3130B | Mouser | www.mouser.com
 | 1554G2GYCL | Hammond Enclosure, polycarbonate, clear cover 4.72H x 3.54W x 3.14D | 1 | $19.77 | $19.77 | 98H1120 | Newark | www.newark.com (http://www.newark.com/hammond/1554g2gycl/enclosure-din-rail-polycarbonate/dp/98H1120?ost=98h1120&ddkey=http%3Aen-US%2FElement14_US%2Fsearch)
BTJ1 |  | Molex Receptacle P/N 03-06-1042-S, 4 POS | 1 | $0.15 | $0.15 | 38C8696 | Newark | www.newark.com
BTP1 |  | Molex Plug P/N 03-06-2042-P, 4 POS | 1 | $0.38 | $0.38 | 38C8709 | Newark | www.newark.com
BTJ2&3 |  | Molex Receptacle P/N 03-06-1023-S, 2 POS | 2 | $0.20 | $0.40 | 26C1314 | Newark | www.newark.com
BTJ2&3 |  | Molex Plug P/N 03-06-2023-P, 2 POS | 2 | $0.20 | $0.40 | 26C1313 | Newark | www.newark.com
 |  | Crimp sockets for BTJ1, Molex P/N 02-06-1132 | 100 | $0.06 | $6.00 | 85C0027 | Newark | www.newark.com
 |  | Crimp pins for BTP1, Molex P/N 02-06-2132 | 100 | $0.09 | $9.00 | 85C0026 | Newark | www.newark.com
J1 |  | Bulgin Buccaneer receptacle, P/N PX0412/06/S/4550, 6 sockets | 1 | $8.11 | $8.11 | 92C2468 | Newark | www.newark.com
P1 |  | Bulgin Buccaneer plug, P/N PX0410/06/P/4550, 6 pins | 1 | $9.51 | $9.51 | 92C2439 | Newark | www.newark.com
 |  | Sealing cap for P1, Bulgin P/N PX0481 | 1 | $2.51 | $2.51 | 92C2477 | Newark | www.newark.com
 |  | Sealing cap for J1, Bulgin P/N PX0480 | 1 | $2.46 | $2.46 | 92C2475 | Newark | www.newark.com
 |  | Solder Contacts for P1, P/N SA3348/1, Pack of 10 | 1 | $9.50 | $9.50 | 92C3200 | Newark | www.newark.com
 |  | Solder Contacts for S1, P/N SA3347/1, Pack of 10 | 1 | $15.12 | $15.12 | 92C3198 | Newark | www.newark.com
 |  |  | TOTAL: |  | $167.24

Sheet: DownriggerInterfaceBox
Downrigger Interface Box: Parts List
Part ID | Part Type | Description | Qty | Cost | Total | Source P/N | Part Source | Notes
 | 2UB3001-W0000W | Plastic Cap for J1, MultiComp | 1 | $1.97 | $1.97 | 20T7280 | Newark | www.newark.com
J1 | 2TJ3003-W05100 | MultiComp P/N 2TJ3003-W05100, RJ45 Jack, 8 Pos, Panel | 1 | $9.30 | $9.30 | 20T7279 | Newark | www.newark.com
J2 | EN3P5FX | Switchcraft Receptacle, 5 position Female, P/N EN3P5FX | 1 | $9.46 | $9.46 | SC264-ND | Digikey | www.digikey.com
J3 | EN3P3FX | Switchcraft Receptacle, 3 position Female, P/N EN3P3FX | 2 | $7.06 | $14.12 | SC260-ND | Digikey | www.digikey.com
P3 | EN3C3MX | Switchcraft Plug, 3 position Male, P/N EN3C3MX | 2 | $5.79 | $11.58 | SC252-ND | Digikey | www.digikey.com
P2 | EN3C5MX | Switchcraft Plug, 5 position Male, P/N EN3C5MX | 1 | $6.35 | $6.35 | SC256-ND | Digikey | www.digikey.com
 | EN3CAP | Switchcraft Weatherproof Caps for J2, J3, P2, and P3 | 6 | $1.85 | $11.10 | SC1174-ND | Digikey | www.digikey.com
 | 1554G2GYCL | Hammond P/N 1554G2GYCL Enclosure | 1 | $19.77 | $19.77 | 98H1120 | Newark | www.newark.com (http://www.newark.com/hammond/1554g2gycl/enclosure-din-rail-polycarbonate/dp/98H1120?ost=98h1120&ddkey=http%3Aen-US%2FElement14_US%2Fsearch)
 |  |  | TOTAL: |  | $83.65

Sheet: BaseStation
Wireless Base Station: Parts List
Part ID | Part Type | Description | Qty | Cost | Total | Source P/N | Part Source | Notes
J1 | 17-200161 | CONEC IP67 USB Connector, USB Female Adapter | 1 | $13.16 | $13.16 | 706-17-200161 | Mouser | www.mouser.com
 | 17-200231 | USB Patch Cord, 2 meters (for use with J1) | 1 | $13.99 | $13.99 | 706-17-200231 | Mouser | www.mouser.com (https://www.mouser.com/ProductDetail/CONEC/17-200231)
 | CSMUAMB5-03M | USB Cable Type A to Mini-B 5 Position, 0.3 meters | 1 | $8.27 | $8.27 | CSMUAMB5-03M | L-Com | www.l-com.com (http://www.l-com.com/usb-premium-usb-cable-type-a-mini-b-5-position-03m)
1A1 | 32400 | Parallax XBee USB Adapter Board | 1 | $24.99 | $24.99 | 32400 | Parallax | www.parallax.com (https://www.parallax.com/product/32400)
U1 | XBee_Pro | Digi Xbee_Pro Wireless Transceiver, XBP9B-DMST-002 | 1 | $39.00 | $39.00 | 602-1299-ND | Digikey | www.digikey.com (https://www.digikey.com/products/en?keywords=602-1299-nd)
 | Antenna,900 MHz | Antenna - 900 MHz, Half Wave Dipole, 2.1 dBi, RPSMA Male, articulating | 1 | $7.63 | $7.63 | 553-1474-ND | Digikey | www.digikey.com (https://www.digikey.com/products/en?keywords=553-1474-nd)
 | 1554G2GYCL | Hammond Enclosure, polycarbonate, clear cover 4.72H x 3.54W x 3.14D | 1 | $19.77 | $19.77 | 98H1120 | Newark | www.newark.com (http://www.newark.com/hammond/1554g2gycl/enclosure-din-rail-polycarbonate/dp/98H1120?ost=98h1120&ddkey=http%3Aen-US%2FElement14_US%2Fsearch)
 | PN-1328-CMB | BUD Enclosure, Polycarbonate with clear cover, 4.53H x 3.54W x 3.15D | 0 | $14.50 | $0.00 | 40T8055 | Newark | (optional enclosure) (http://www.newark.com/)
 |  |  | TOTAL: |  | $126.81

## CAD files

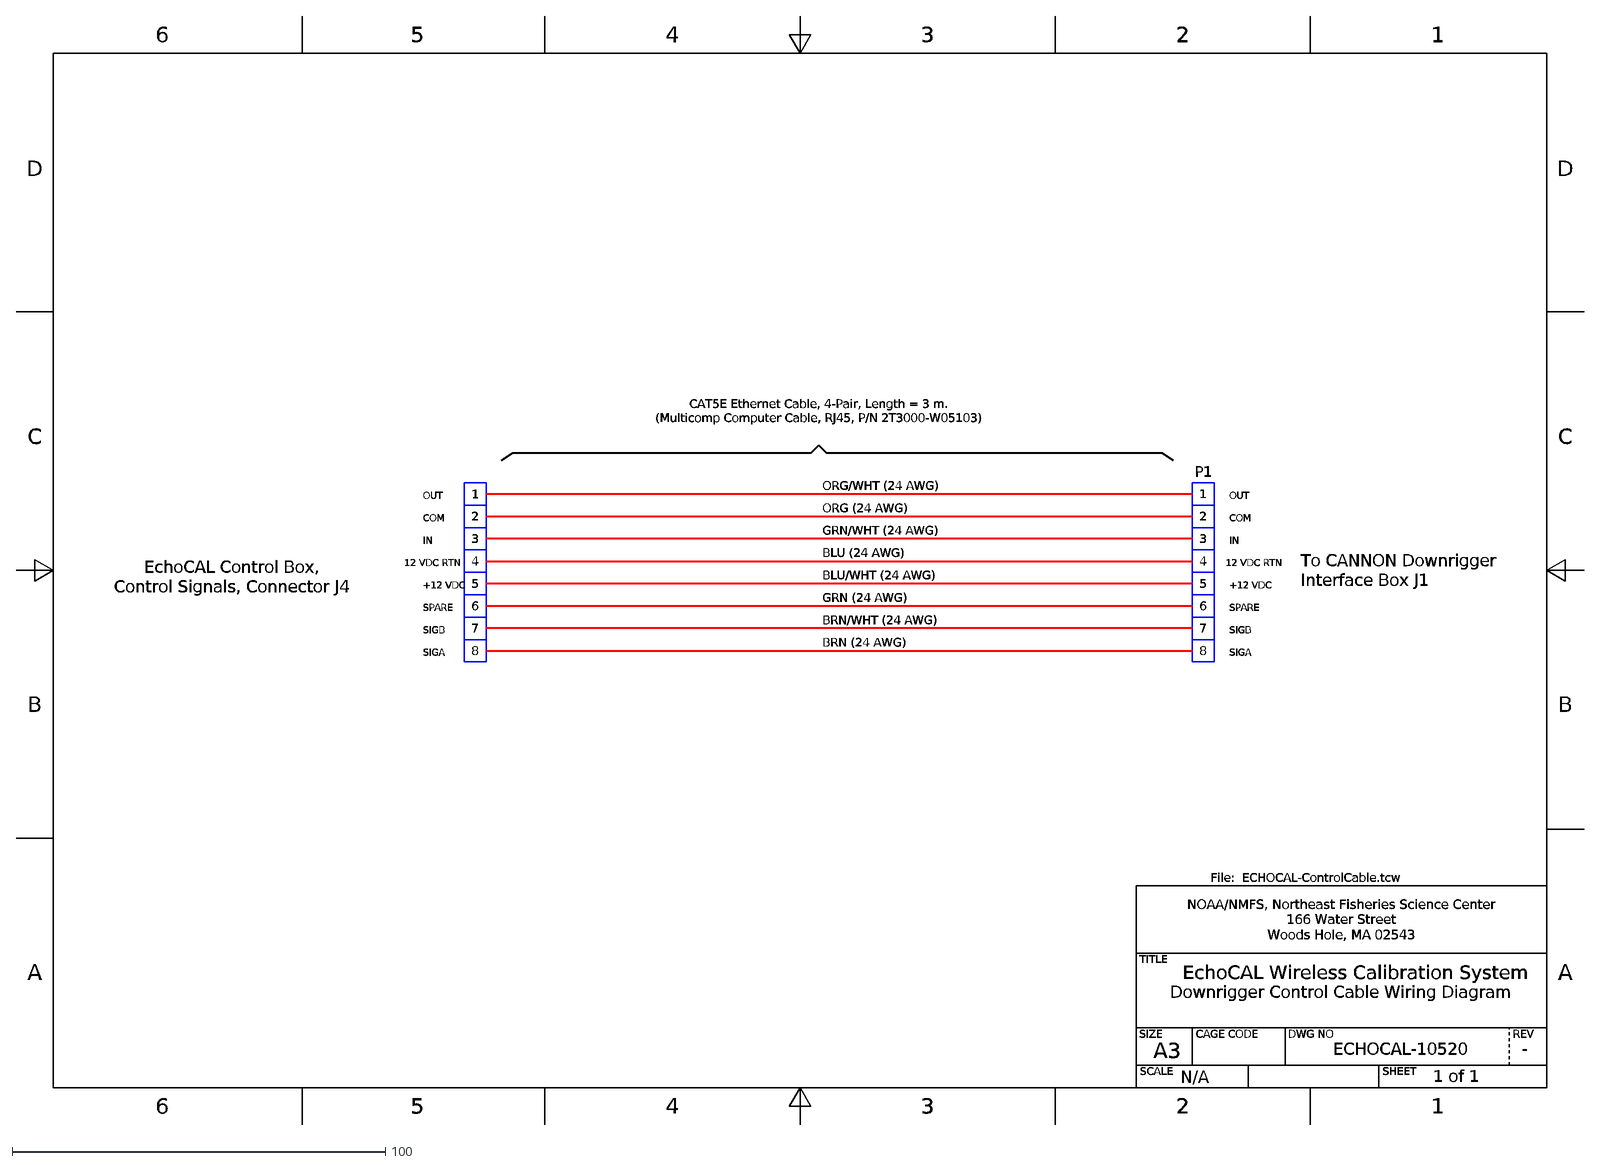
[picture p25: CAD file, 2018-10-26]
DesignFiles/WiringDiagrams/ECHOCAL-ControlCable.DXF
A3
D
C
B
A
6
5
4
3
2
1
SCALE
SIZE
CAGE CODE
DWG NO
SHEET
REV
TITLE
NOAA/NMFS, Northeast Fisheries Science Center
166 Water Street Woods Hole, MA 02543
ECHOCAL-10520
1 of 1
-
N/A
EchoCAL Wireless Calibration System
Downrigger Control Cable Wiring Diagram
EchoCAL Control Box, Control Signals, Connector J4
P1
CAT5E Ethernet Cable, 4-Pair, Length = 3 m. (Multicomp Computer Cable, RJ45, P/N 2T3000-W05103)
ORG/WHT (24 AWG)
To CANNON Downrigger Interface Box J1
7
8
ORG (24 AWG)
GRN/WHT (24 AWG)
BLU (24 AWG)
BLU/WHT (24 AWG)
GRN (24 AWG)
BRN/WHT (24 AWG)
BRN (24 AWG)
OUT
COM
IN
12 VDC RTN
+12 VDC
SPARE
SIGB
SIGA
File: ECHOCAL-ControlCable.tcw

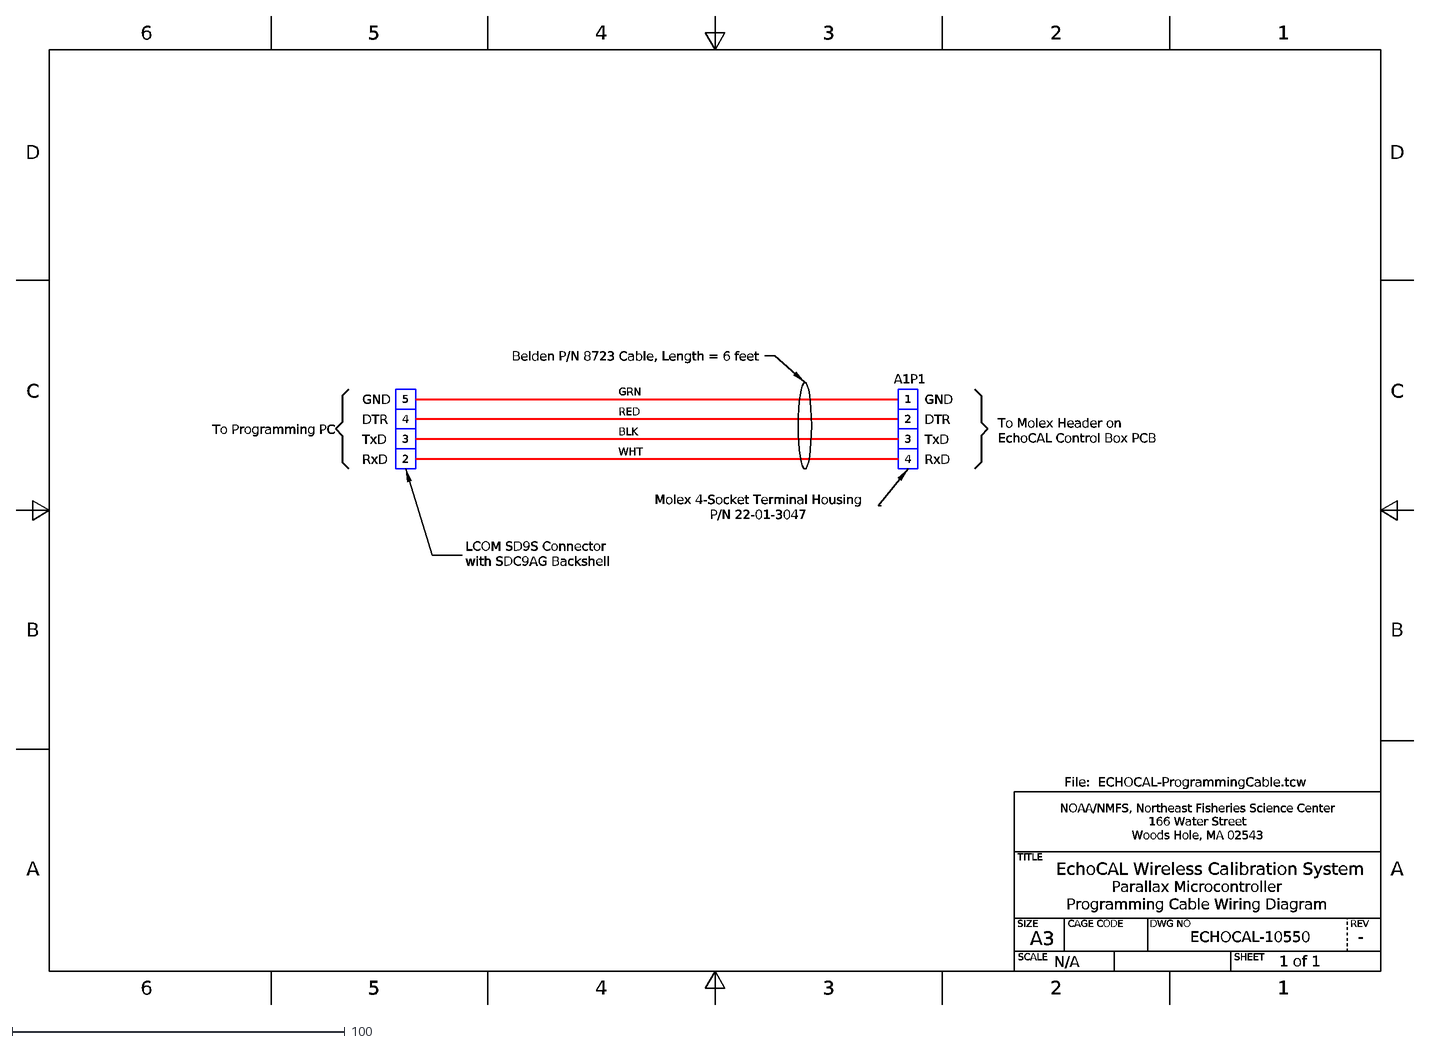
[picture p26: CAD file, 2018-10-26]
DesignFiles/WiringDiagrams/ECHOCAL-ProgrammingCable.DXF
A3
D
C
B
A
6
5
4
3
2
1
SCALE
SIZE
CAGE CODE
DWG NO
SHEET
REV
TITLE
NOAA/NMFS, Northeast Fisheries Science Center
166 Water Street Woods Hole, MA 02543
ECHOCAL-10550
1 of 1
-
N/A
EchoCAL Wireless Calibration System
Parallax Microcontroller Programming Cable Wiring Diagram
GRN
RED
A1P1
Belden P/N 8723 Cable, Length = 6 feet
GND
DTR
File: ECHOCAL-ProgrammingCable.tcw
TxD
RxD
To Molex Header on EchoCAL Control Box PCB
To Programming PC
Molex 4-Socket Terminal Housing P/N 22-01-3047
LCOM SD9S Connector with SDC9AG Backshell
BLK
WHT

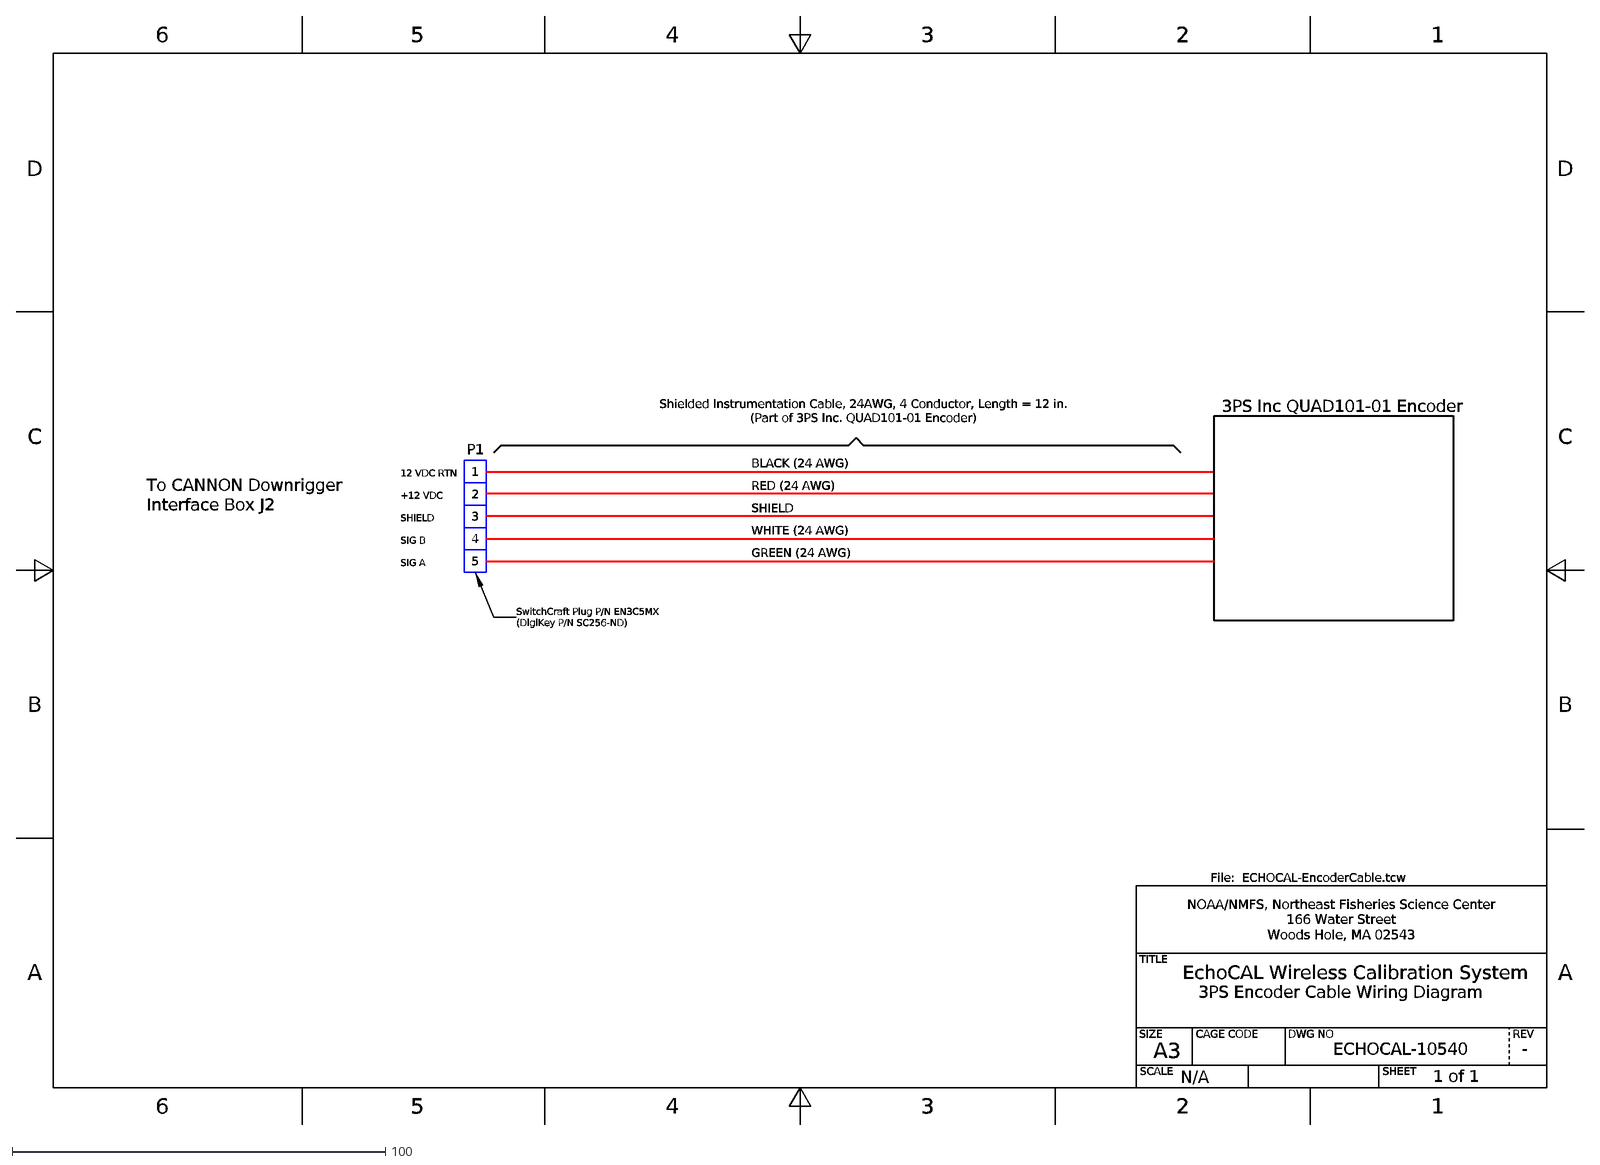
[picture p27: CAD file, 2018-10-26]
DesignFiles/WiringDiagrams/ECHOCAL-EncoderCable.DXF
A3
D
C
B
A
6
5
4
3
2
1
SCALE
SIZE
CAGE CODE
DWG NO
SHEET
REV
TITLE
NOAA/NMFS, Northeast Fisheries Science Center
166 Water Street Woods Hole, MA 02543
ECHOCAL-10540
1 of 1
-
N/A
EchoCAL Wireless Calibration System
3PS Encoder Cable Wiring Diagram
To CANNON Downrigger Interface Box J2
Shielded Instrumentation Cable, 24AWG, 4 Conductor, Length = 12 in. (Part of 3PS Inc. QUAD101-01 Encoder)
RED (24 AWG)
SHIELD
3PS Inc QUAD101-01 Encoder
SwitchCraft Plug P/N EN3C5MX (DigiKey P/N SC256-ND)
P1
BLACK (24 AWG)
WHITE (24 AWG)
GREEN (24 AWG)
12 VDC RTN
+12 VDC
SIG B
SIG A
File: ECHOCAL-EncoderCable.tcw

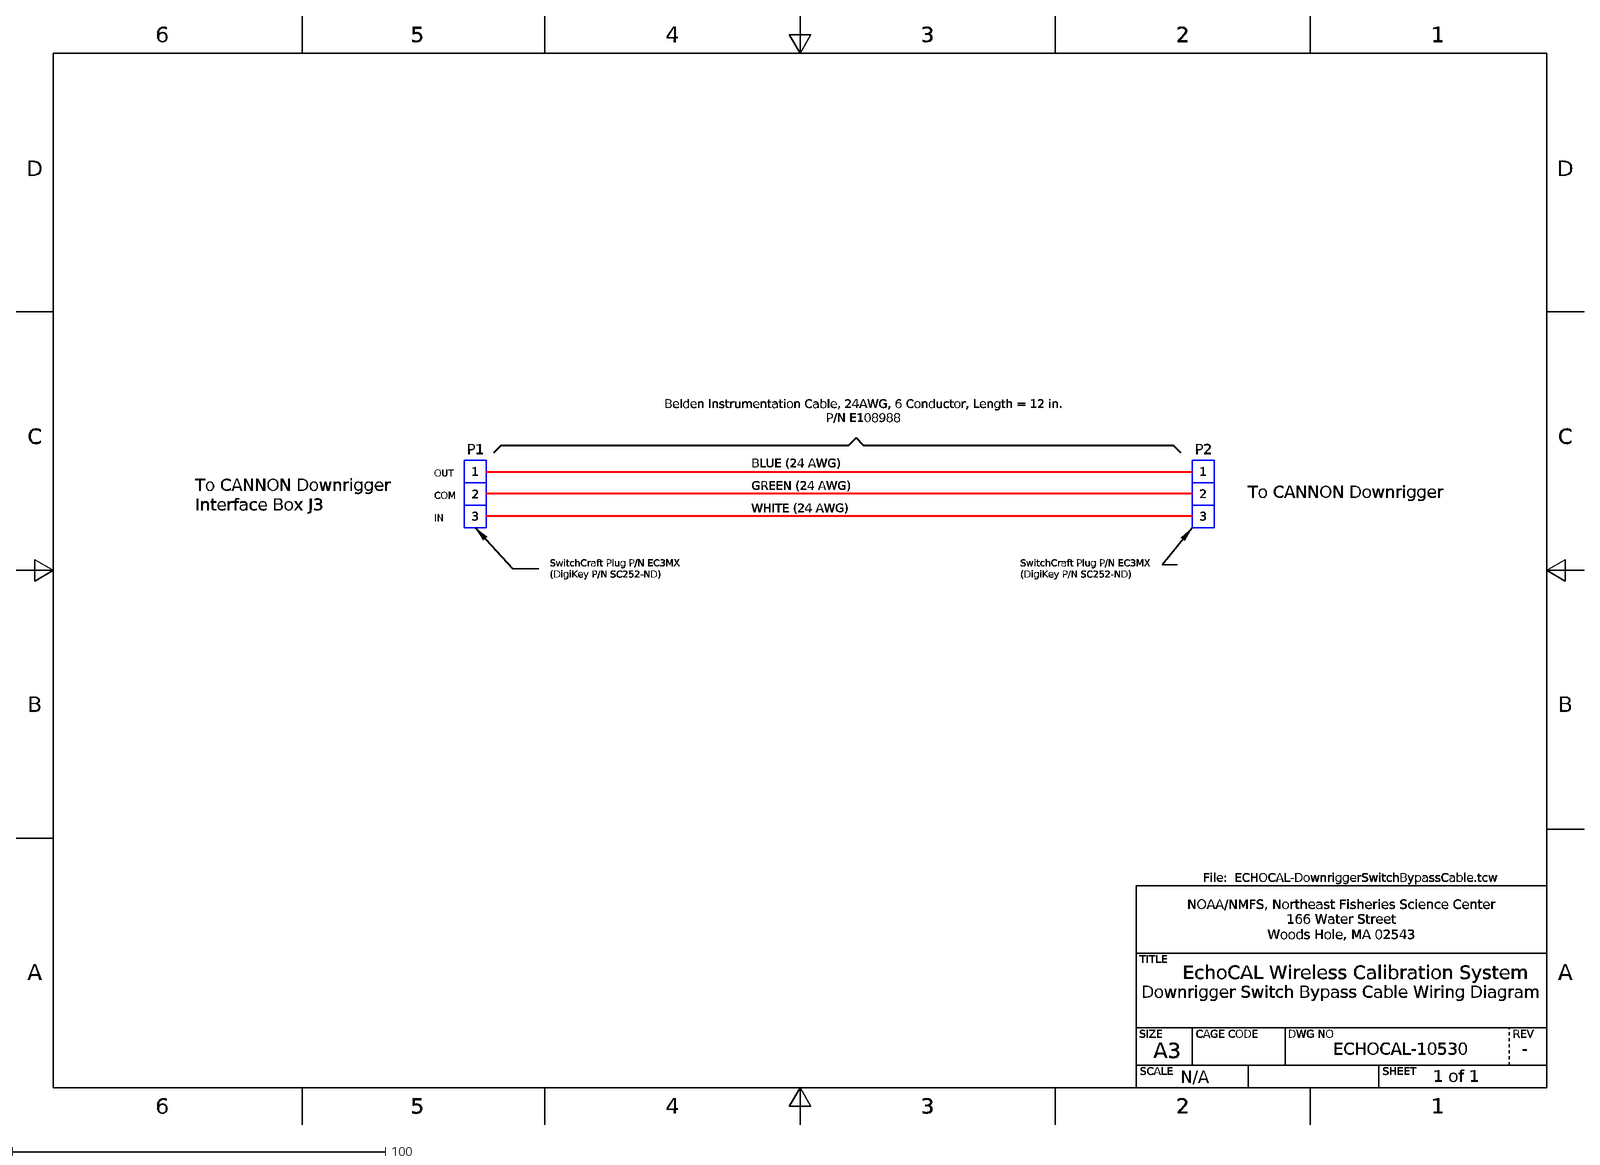
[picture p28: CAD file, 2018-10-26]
DesignFiles/WiringDiagrams/ECHOCAL-DownriggerSwitchBypassCable.DXF
A3
D
C
B
A
6
5
4
3
2
1
SCALE
SIZE
CAGE CODE
DWG NO
SHEET
REV
TITLE
NOAA/NMFS, Northeast Fisheries Science Center
166 Water Street Woods Hole, MA 02543
ECHOCAL-10530
1 of 1
-
N/A
EchoCAL Wireless Calibration System
Downrigger Switch Bypass Cable Wiring Diagram
To CANNON Downrigger Interface Box J3
SwitchCraft Plug P/N EC3MX (DigiKey P/N SC252-ND)
P2
Belden Instrumentation Cable, 24AWG, 6 Conductor, Length = 12 in. P/N E108988
GREEN (24 AWG)
WHITE (24 AWG)
To CANNON Downrigger
P1
BLUE (24 AWG)
OUT
COM
IN
File: ECHOCAL-DownriggerSwitchBypassCable.tcw

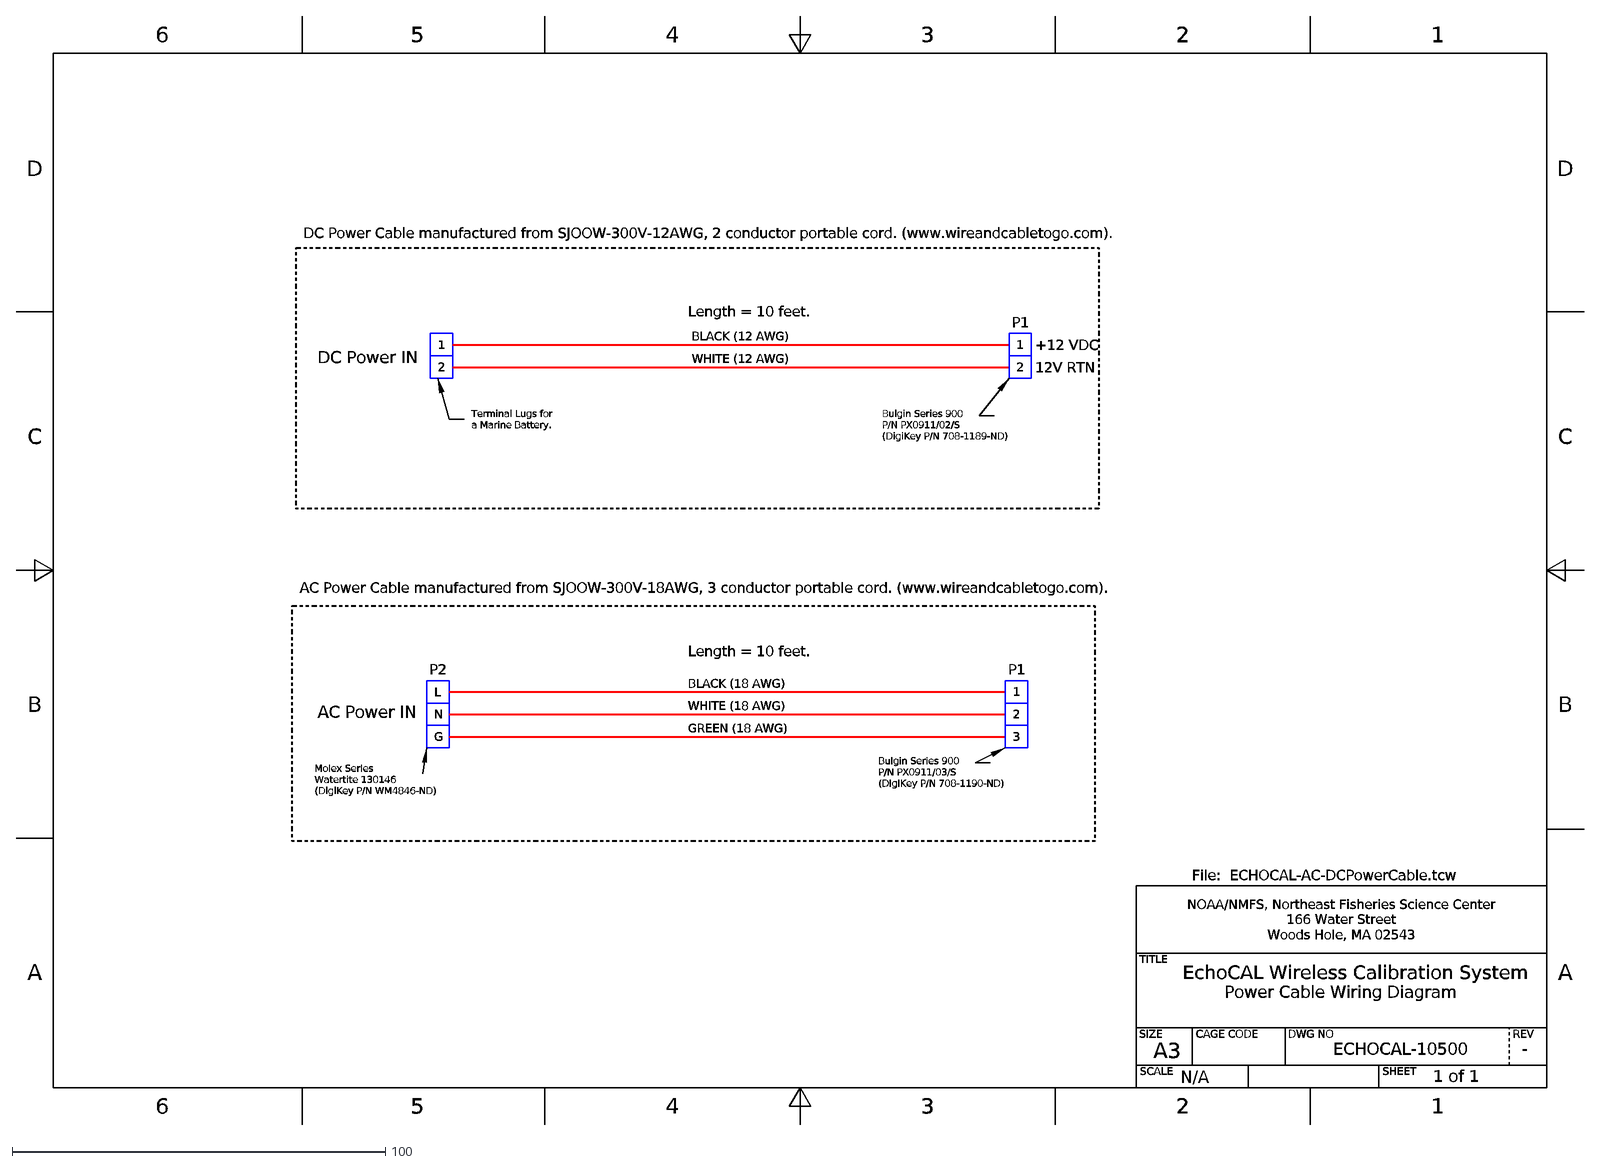
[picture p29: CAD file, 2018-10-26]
DesignFiles/WiringDiagrams/ECHOCAL-AC-DCPowerCable.DXF
A3
D
C
B
A
6
5
4
3
2
1
SCALE
SIZE
CAGE CODE
DWG NO
SHEET
REV
TITLE
NOAA/NMFS, Northeast Fisheries Science Center
166 Water Street Woods Hole, MA 02543
ECHOCAL-10500
1 of 1
-
N/A
EchoCAL Wireless Calibration System
Power Cable Wiring Diagram
P2
AC Power IN
L
N
G
BLACK (18 AWG)
WHITE (18 AWG)
GREEN (18 AWG)
Molex Series Watertite 130146 (DigiKey P/N WM4846-ND)
Bulgin Series 900 P/N PX0911/03/S (DigiKey P/N 708-1190-ND)
P1
DC Power IN
BLACK (12 AWG)
WHITE (12 AWG)
Bulgin Series 900 P/N PX0911/02/S (DigiKey P/N 708-1189-ND)
Terminal Lugs for a Marine Battery.
DC Power Cable manufactured from SJOOW-300V-12AWG, 2 conductor portable cord. (www.wireandcabletogo.com).
Length = 10 feet.
AC Power Cable manufactured from SJOOW-300V-18AWG, 3 conductor portable cord. (www.wireandcabletogo.com).
+12 VDC
12V RTN
File: ECHOCAL-AC-DCPowerCable.tcw

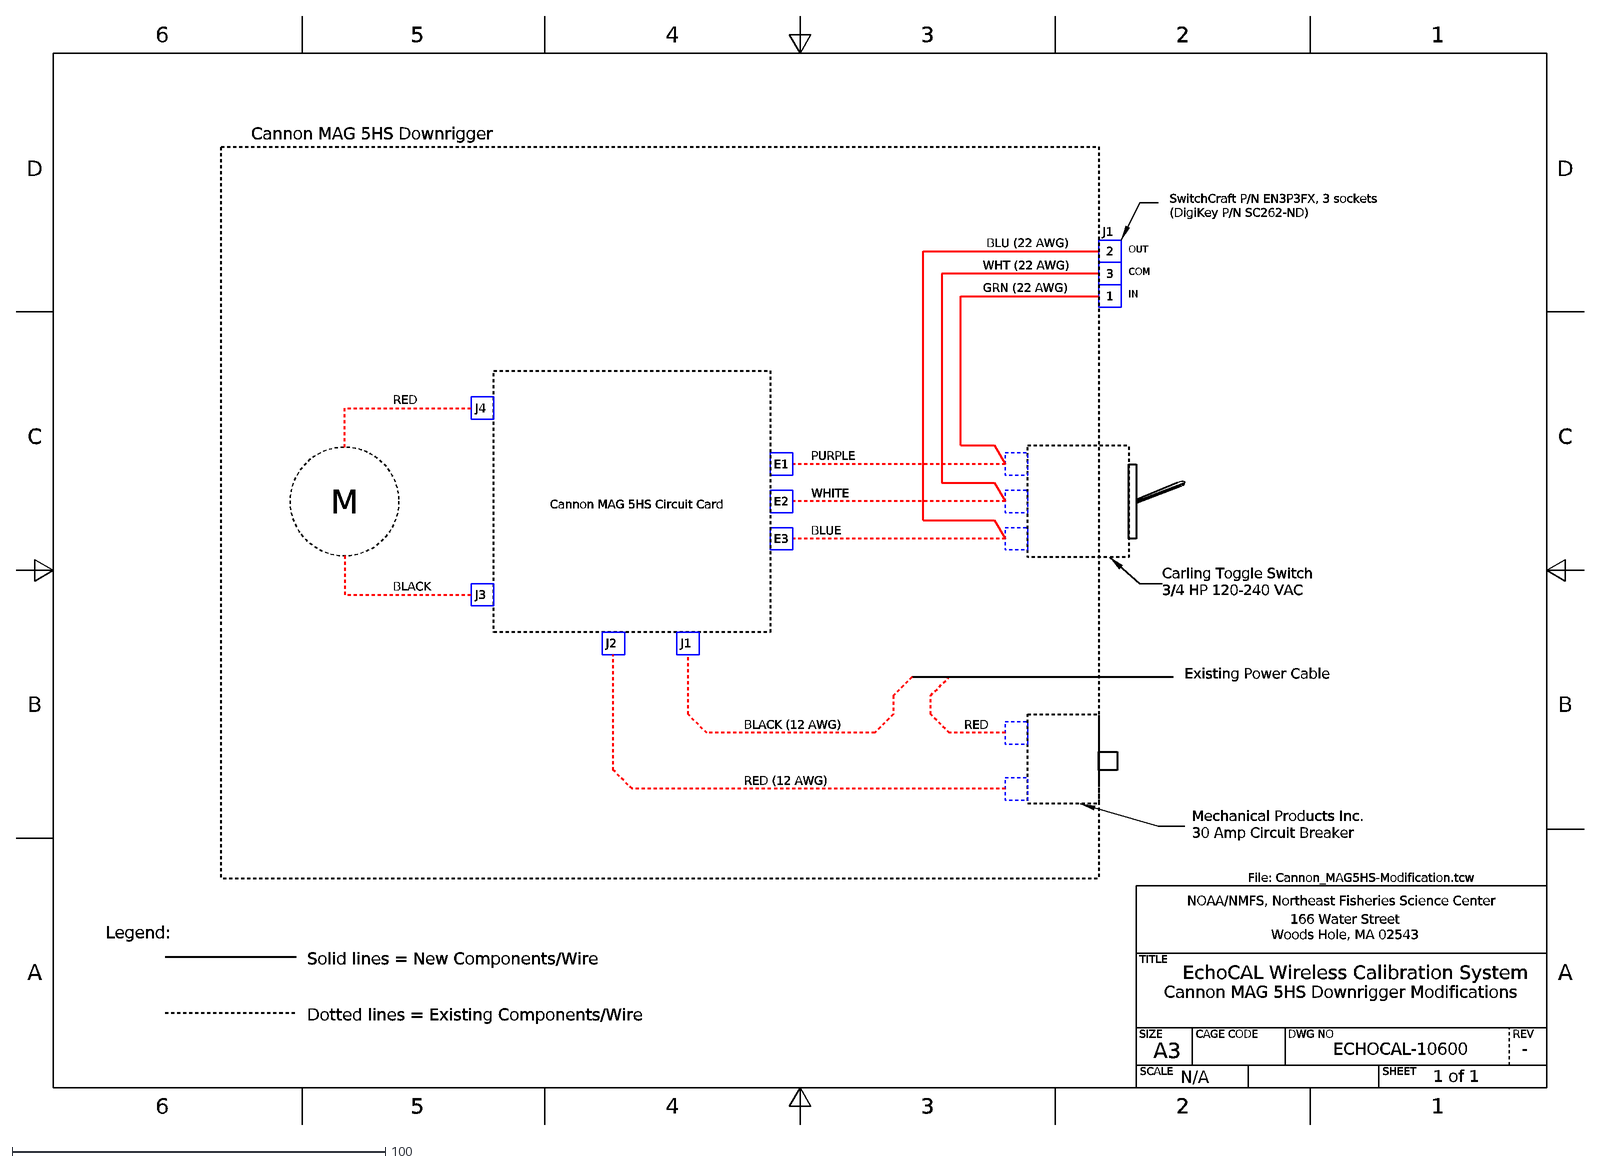
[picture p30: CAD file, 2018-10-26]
DesignFiles/WiringDiagrams/Cannon_MAG5HS_Modification.DXF
A3
D
C
B
A
6
5
4
3
2
1
SCALE
SIZE
CAGE CODE
DWG NO
SHEET
REV
TITLE
NOAA/NMFS, Northeast Fisheries Science Center
166 Water Street Woods Hole, MA 02543
ECHOCAL-10600
1 of 1
-
N/A
EchoCAL Wireless Calibration System
Cannon MAG 5HS Downrigger Modifications
J1
WHT (22 AWG)
GRN (22 AWG)
BLU (22 AWG)
OUT
COM
IN
SwitchCraft P/N EN3P3FX, 3 sockets (DigiKey P/N SC262-ND)
M
PURPLE
WHITE
BLUE
E1
E2
E3
J4
J3
RED
BLACK
Carling Toggle Switch 3/4 HP 120-240 VAC
J2
BLACK (12 AWG)
RED (12 AWG)
Existing Power Cable
Mechanical Products Inc. 30 Amp Circuit Breaker
Cannon MAG 5HS Downrigger
Legend:
Solid lines = New Components/Wire
Dotted lines = Existing Components/Wire
Cannon MAG 5HS Circuit Card
File: Cannon_MAG5HS-Modification.tcw

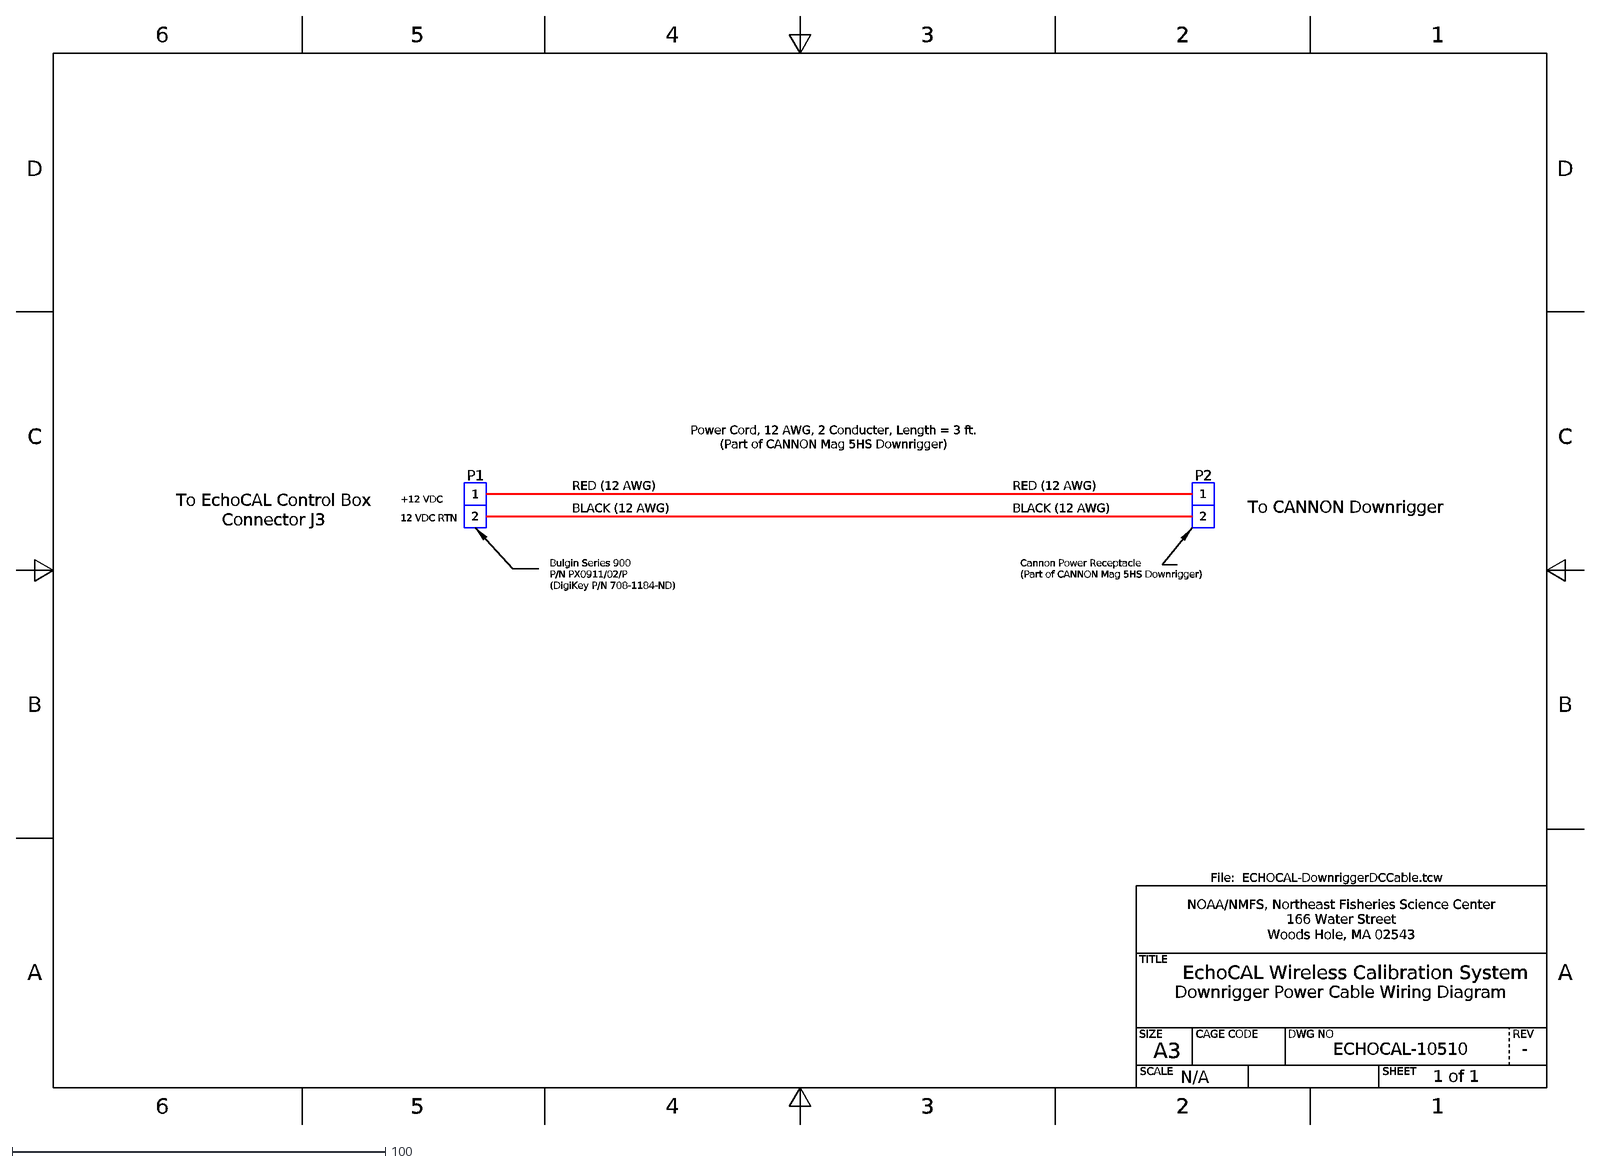
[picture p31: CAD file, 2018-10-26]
DesignFiles/WiringDiagrams/ECHOCAL-DownriggerDCCable.DXF
A3
D
C
B
A
6
5
4
3
2
1
SCALE
SIZE
CAGE CODE
DWG NO
SHEET
REV
TITLE
NOAA/NMFS, Northeast Fisheries Science Center
166 Water Street Woods Hole, MA 02543
ECHOCAL-10510
1 of 1
-
N/A
EchoCAL Wireless Calibration System
Downrigger Power Cable Wiring Diagram
To EchoCAL Control Box Connector J3
Cannon Power Receptacle (Part of CANNON Mag 5HS Downrigger)
P2
RED (12 AWG)
BLACK (12 AWG)
To CANNON Downrigger
Bulgin Series 900 P/N PX0911/02/P (DigiKey P/N 708-1184-ND)
P1
Power Cord, 12 AWG, 2 Conducter, Length = 3 ft. (Part of CANNON Mag 5HS Downrigger)
+12 VDC
12 VDC RTN
File: ECHOCAL-DownriggerDCCable.tcw

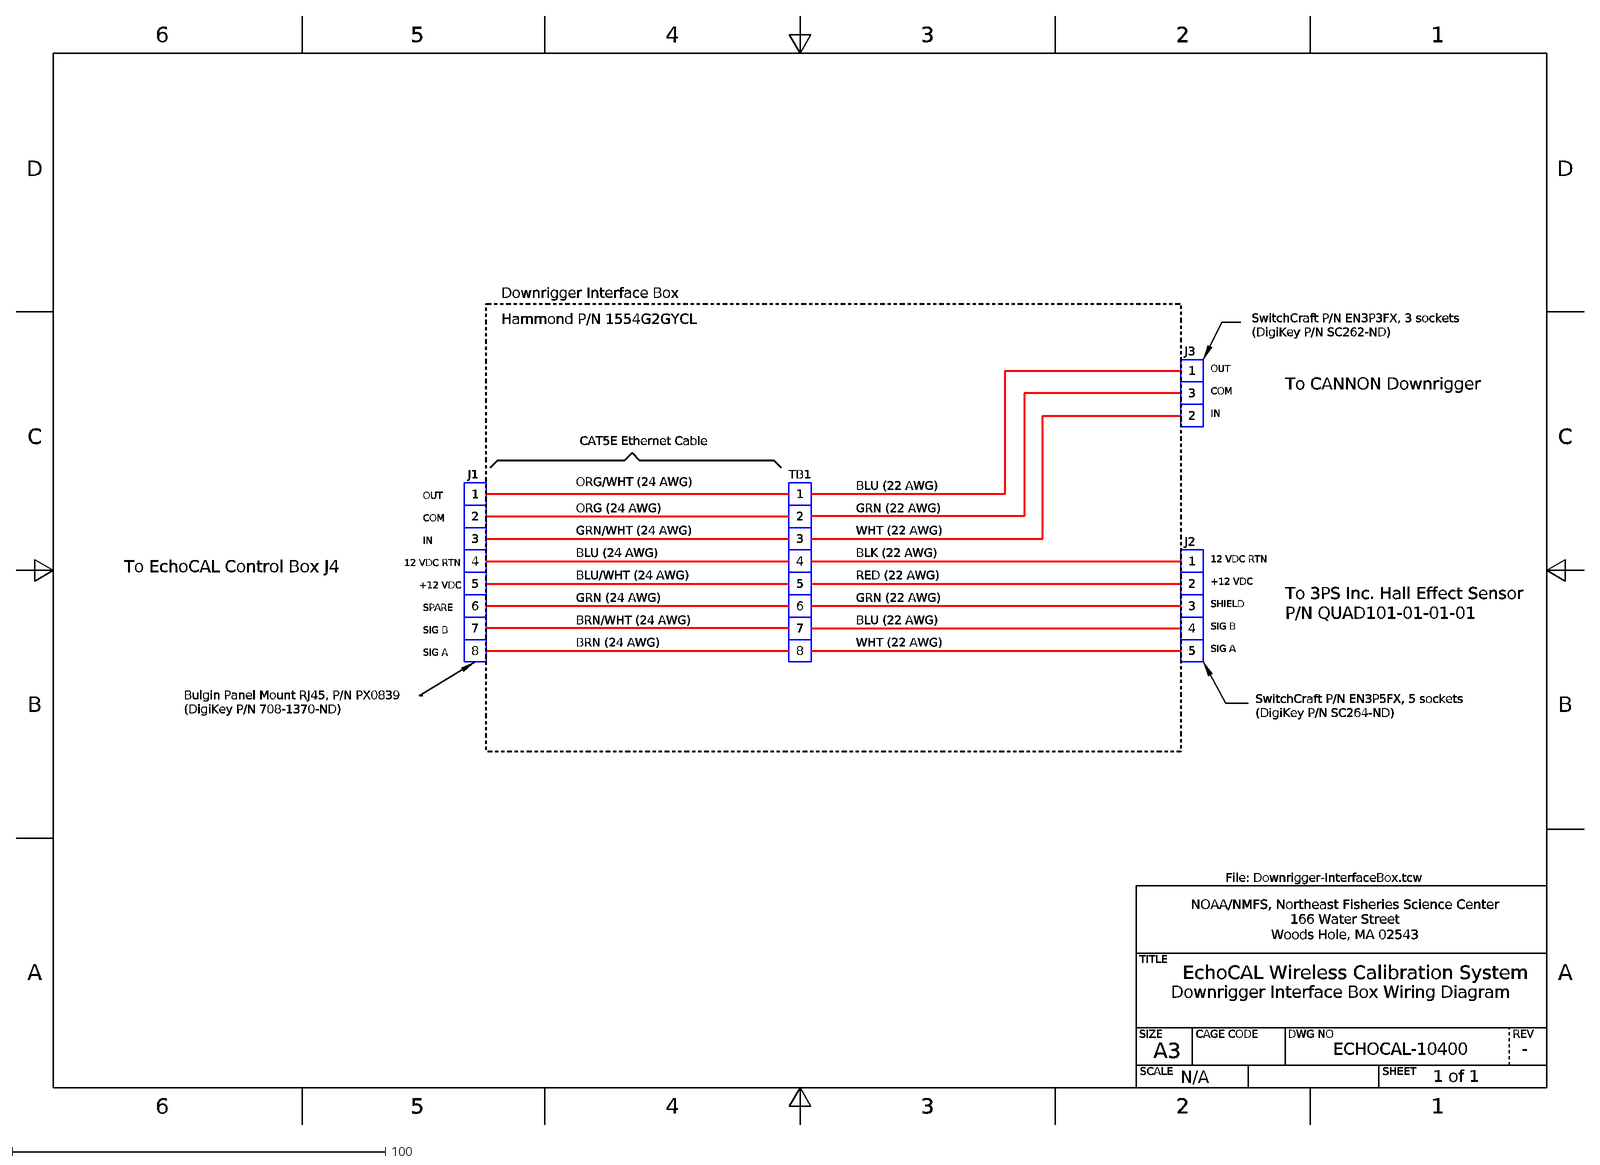
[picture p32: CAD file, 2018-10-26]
DesignFiles/WiringDiagrams/Downrigger-InterfaceBox.DXF
A3
D
C
B
A
6
5
4
3
2
1
SCALE
SIZE
CAGE CODE
DWG NO
SHEET
REV
TITLE
NOAA/NMFS, Northeast Fisheries Science Center
166 Water Street Woods Hole, MA 02543
ECHOCAL-10400
1 of 1
-
N/A
EchoCAL Wireless Calibration System
Downrigger Interface Box Wiring Diagram
To EchoCAL Control Box J4
To CANNON Downrigger
7
8
OUT
COM
IN
12 VDC RTN
+12 VDC
SPARE
SIG B
SIG A
J1
TB1
J3
J2
To 3PS Inc. Hall Effect Sensor P/N QUAD101-01-01-01
ORG/WHT (24 AWG)
ORG (24 AWG)
GRN/WHT (24 AWG)
BLU (24 AWG)
BLU/WHT (24 AWG)
GRN (24 AWG)
BRN/WHT (24 AWG)
BRN (24 AWG)
CAT5E Ethernet Cable
BLK (22 AWG)
RED (22 AWG)
GRN (22 AWG)
BLU (22 AWG)
WHT (22 AWG)
SHIELD
Downrigger Interface Box
Hammond P/N 1554G2GYCL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

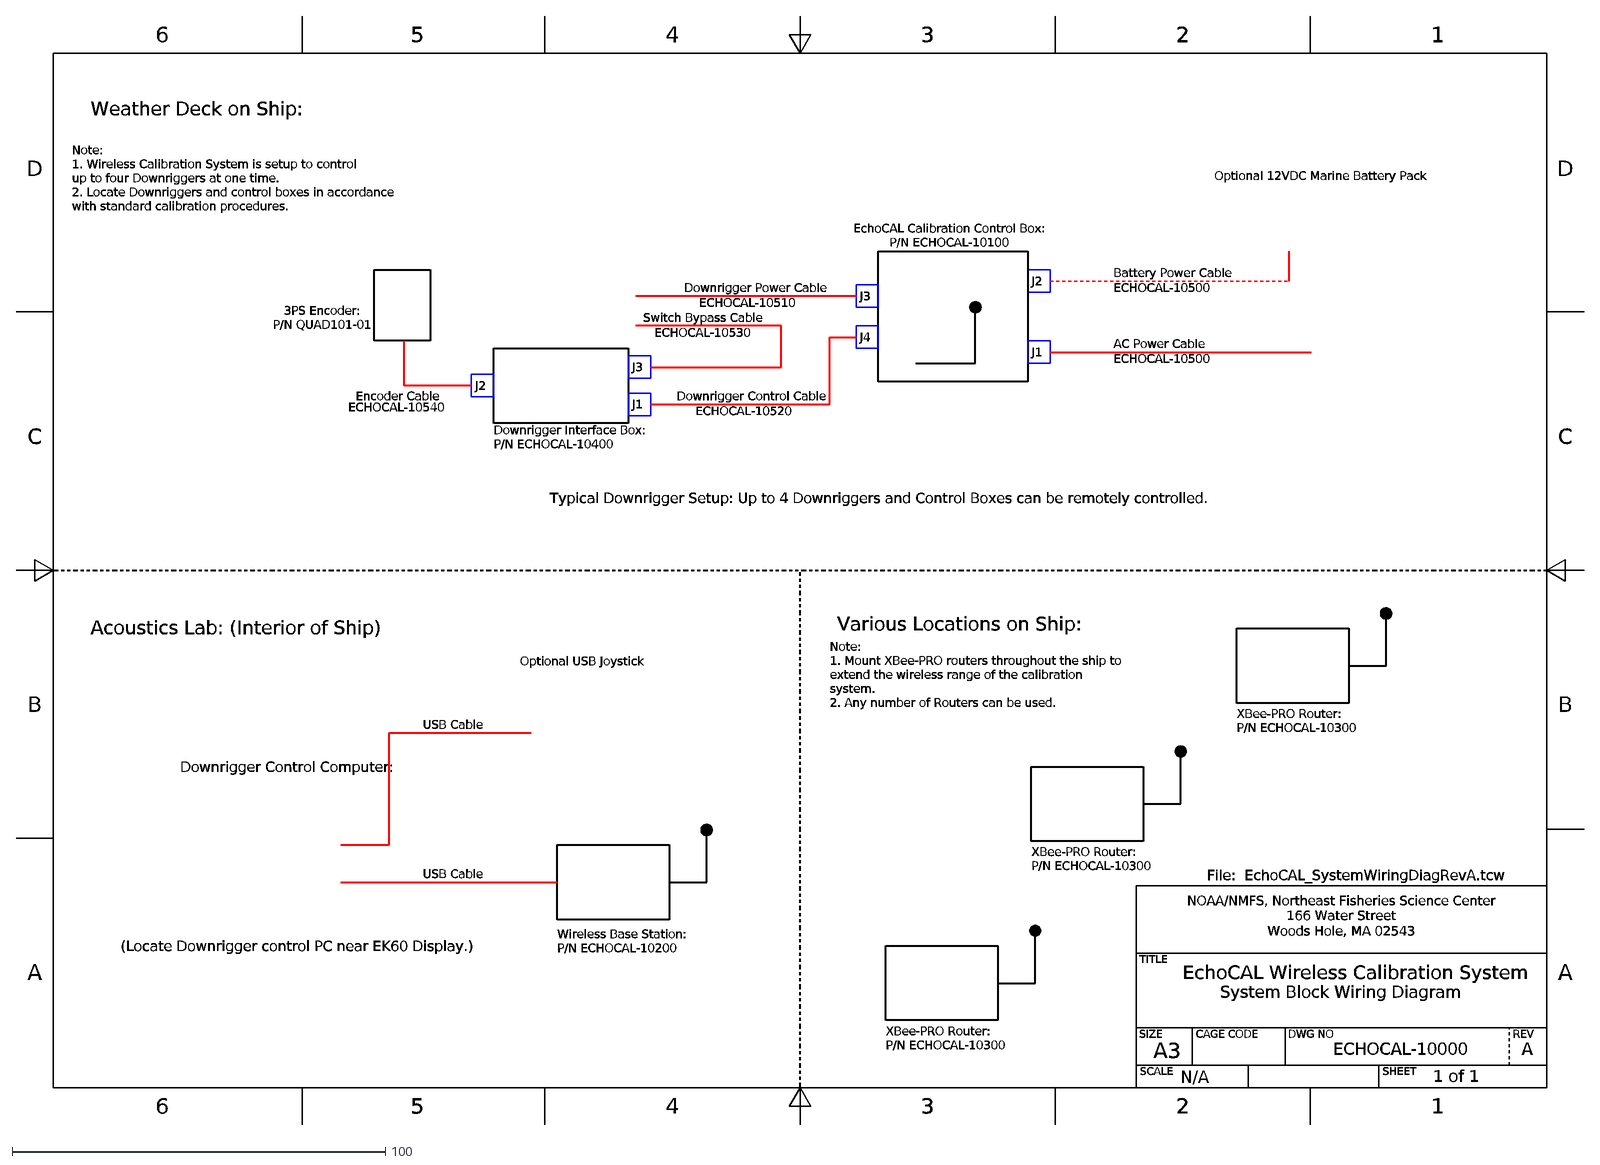
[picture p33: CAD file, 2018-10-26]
DesignFiles/WiringDiagrams/EchoCAL_SystemWiringDiagRevA.DXF
A3
D
C
B
A
6
5
4
3
2
1
SCALE
SIZE
CAGE CODE
DWG NO
SHEET
REV
TITLE
NOAA/NMFS, Northeast Fisheries Science Center
166 Water Street Woods Hole, MA 02543
ECHOCAL-10000
1 of 1
N/A
EchoCAL Wireless Calibration System
System Block Wiring Diagram
USB Cable
Wireless Base Station: P/N ECHOCAL-10200
XBee-PRO Router: P/N ECHOCAL-10300
J2
J1
J3
J4
EchoCAL Calibration Control Box: P/N ECHOCAL-10100
Downrigger Power Cable
ECHOCAL-10510
Downrigger Control Cable
Switch Bypass Cable
Encoder Cable
ECHOCAL-10530
ECHOCAL-10520
ECHOCAL-10540
Downrigger Interface Box: P/N ECHOCAL-10400
3PS Encoder: P/N QUAD101-01
Battery Power Cable
AC Power Cable
ECHOCAL-10500
Acoustics Lab: (Interior of Ship)
Weather Deck on Ship:
Note: 1. Wireless Calibration System is setup to control up to four Downriggers at one time. 2. Locate Downriggers and control boxes in accordance with standard
Various Locations on Ship:
Note: 1. Mount XBee-PRO routers throughout the ship to extend the wireless range of the calibration system. 2. Any number of Routers can be used.
Typical Downrigger Setup: Up to 4 Downriggers and Control Boxes can be remotely controlled.
(Locate Downrigger control PC near EK60 Display.)
Downrigger Control Computer:
File: EchoCAL_SystemWiringDiagRevA.tcw
Optional USB Joystick
Optional 12VDC Marine Battery Pack

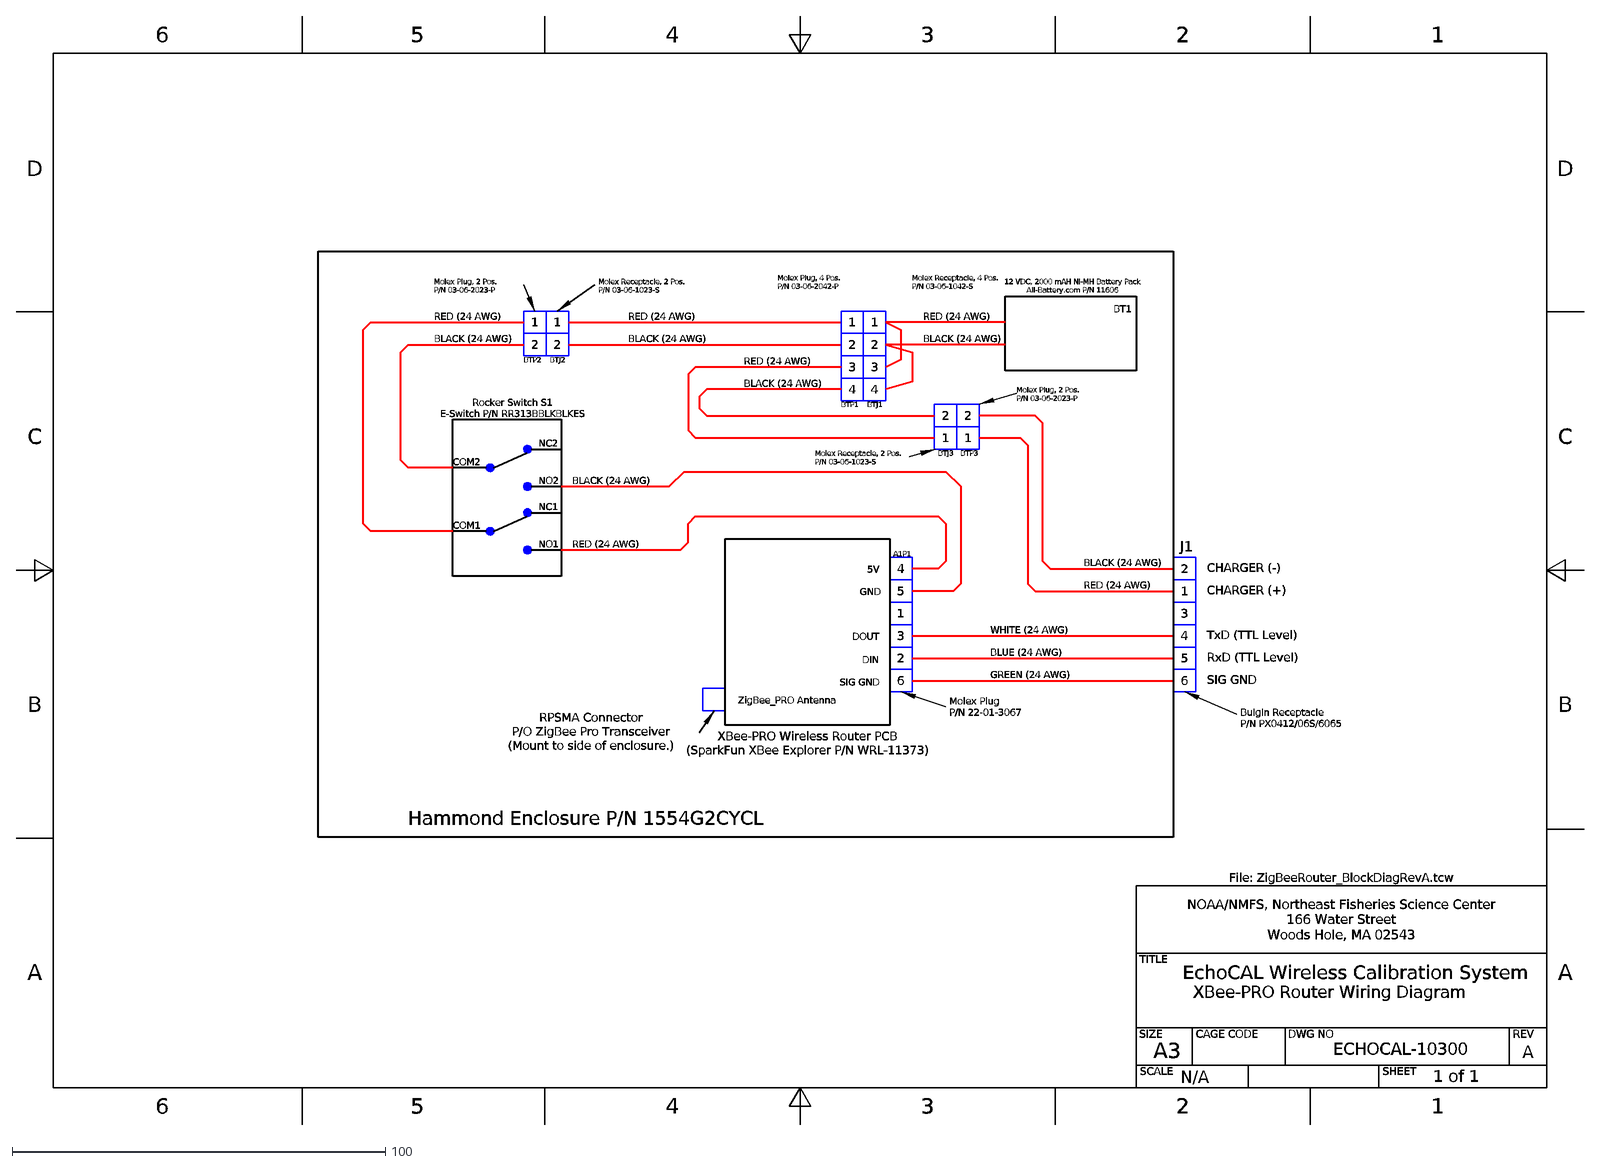
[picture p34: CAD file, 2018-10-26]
DesignFiles/WiringDiagrams/ZigBeeRouter_BlockDiagRevA.DXF
A3
D
C
B
A
6
5
4
3
2
1
SCALE
SIZE
CAGE CODE
DWG NO
SHEET
REV
TITLE
NOAA/NMFS, Northeast Fisheries Science Center
166 Water Street Woods Hole, MA 02543
ECHOCAL-10300
1 of 1
N/A
EchoCAL Wireless Calibration System
XBee-PRO Router Wiring Diagram
SIG GND
XBee-PRO Wireless Router PCB (SparkFun XBee Explorer P/N WRL-11373)
A1P1
J1
DOUT
DIN
ZigBee_PRO Antenna
BT1
12 VDC, 2000 mAH Ni-MH Battery Pack All-Battery.com P/N 11606
COM1
NC1
NO1
COM2
NC2
NO2
RED (24 AWG)
BLACK (24 AWG)
Molex Plug, 2 Pos. P/N 03-06-2023-P
Molex Receptacle, 2 Pos. P/N 03-06-1023-S
Rocker Switch S1 E-Switch P/N RR313BBLKBLKES
Bulgin Receptacle P/N PX0412/06S/6065
Molex Plug P/N 22-01-3067
WHITE (24 AWG)
BLUE (24 AWG)
GREEN (24 AWG)
Hammond Enclosure P/N 1554G2CYCL
BTP2
BTJ2
File: ZigBeeRouter_BlockDiagRevA.tcw
GND
5V
BTJ1
BTP1
BTJ3
BTP3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

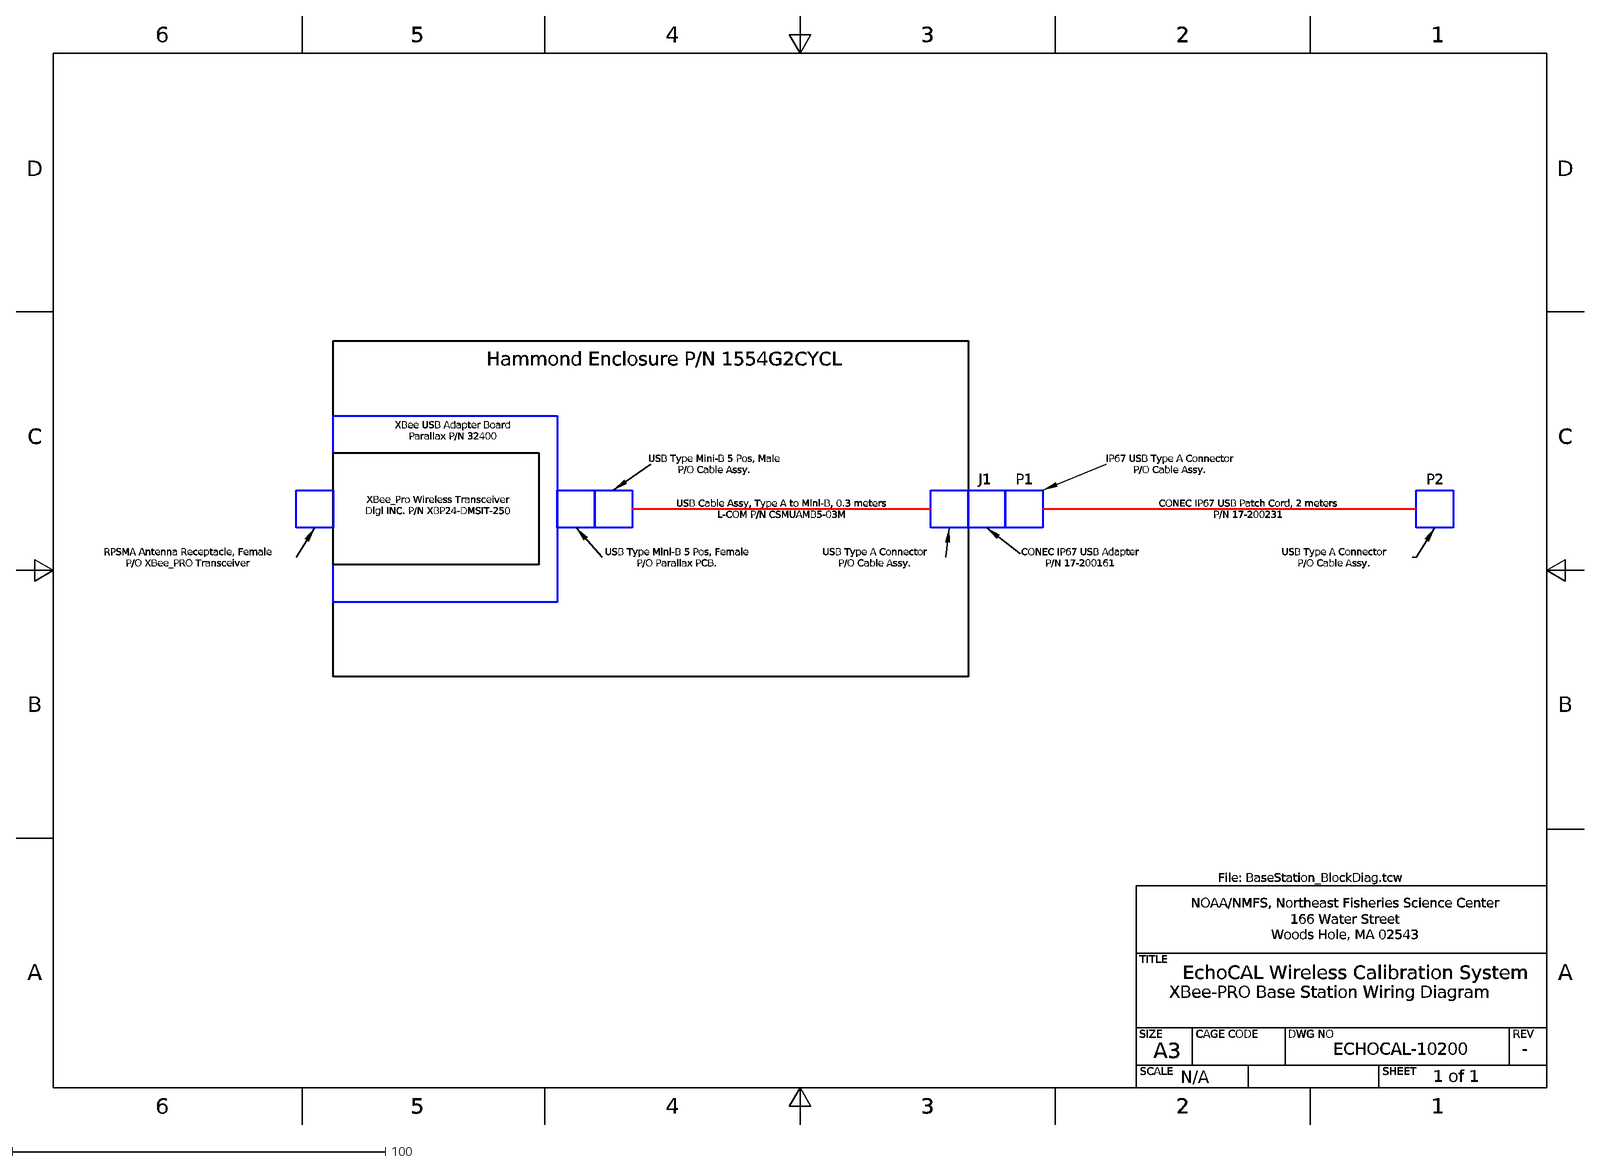
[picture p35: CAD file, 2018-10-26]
DesignFiles/WiringDiagrams/BaseStation_BlockDiag.DXF
A3
D
C
B
A
6
5
4
3
2
1
SCALE
SIZE
CAGE CODE
DWG NO
SHEET
REV
TITLE
NOAA/NMFS, Northeast Fisheries Science Center
166 Water Street Woods Hole, MA 02543
ECHOCAL-10200
1 of 1
-
N/A
EchoCAL Wireless Calibration System
XBee-PRO Base Station Wiring Diagram
Hammond Enclosure P/N 1554G2CYCL
J1
P1
CONEC IP67 USB Patch Cord, 2 meters P/N 17-200231
CONEC IP67 USB Adapter P/N 17-200161
XBee USB Adapter Board Parallax P/N 32400
XBee_Pro Wireless Transceiver Digi INC. P/N XBP24-DMSIT-250
USB Cable Assy, Type A to Mini-B, 0.3 meters L-COM P/N CSMUAMB5-03M
P2
USB Type A Connector P/O Cable Assy.
IP67 USB Type A Connector P/O Cable Assy.
USB Type Mini-B 5 Pos, Male P/O Cable Assy.
USB Type Mini-B 5 Pos, Female P/O Parallax PCB.
RPSMA Antenna Receptacle, Female P/O XBee_PRO Transceiver
File: BaseStation_BlockDiag.tcw

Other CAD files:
DesignFiles/WiringDiagrams/EchoCAL_CntrlBox_DiagRevB.DXF

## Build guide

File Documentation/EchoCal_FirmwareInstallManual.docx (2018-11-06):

NEFSC Echosounder Calibration System

(EchoCAL)

Microcontroller Firmware Installation Manual

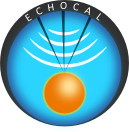
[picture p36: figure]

# 1.0 Introduction:

The EchoCAL Control Box (Figure 1) uses a custom-built printed circuit board (PCB) which incorporates a Parallax Propeller microcontroller (https://www.parallax.com/product/p8x32a-d40) to interact with the Canon Downriggers as well as provide wireless communications with the controlling PC. This microcontroller is programmed using the Propeller Tool Integrated Development Environment (IDE). (https://www.parallax.com/downloads/propeller-tool-software-windows-spin-assembly) Each EchoCAL Control Box requires a unique serial number to allow the EchoCAL Graphical User Interface (GUI) software to reliably interact with each downrigger station. The following instructions will tell the user how to program the microcontroller as well as assign a unique serial number to the box.

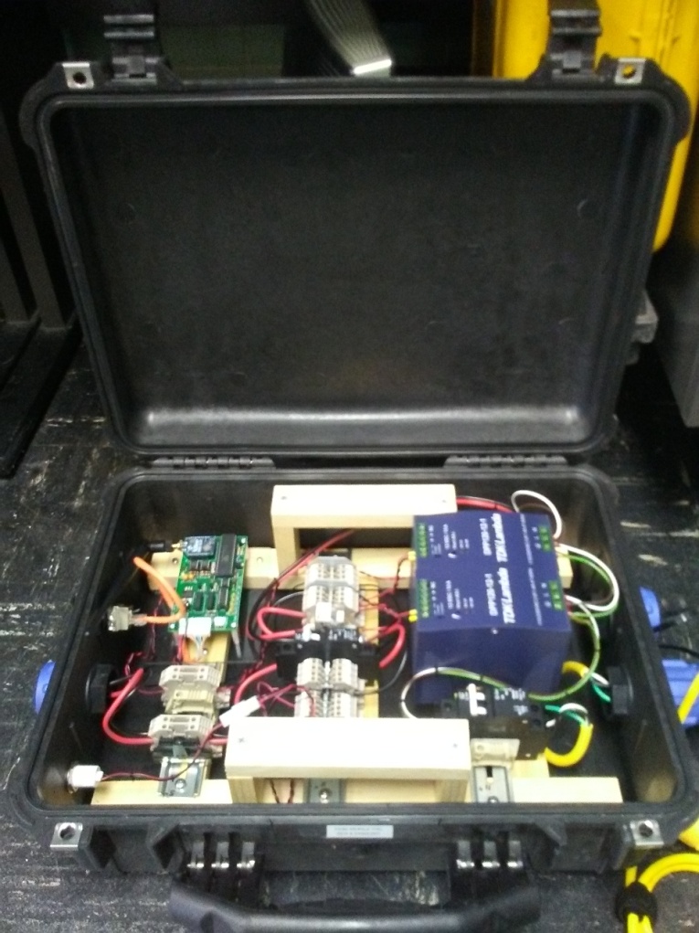
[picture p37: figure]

Figure 1: EchoCAL Control Box Assembly.

# 2.0 Installing Microcontroller Firmware:

- Prior to firmware installation, open the EchoCAL Control Box, and connect the EchoCAL Control Box PCB serial header to a Window’s based PC’s serial port using the ECHOCAL-10550 Programming cable. (See Figure 2.)

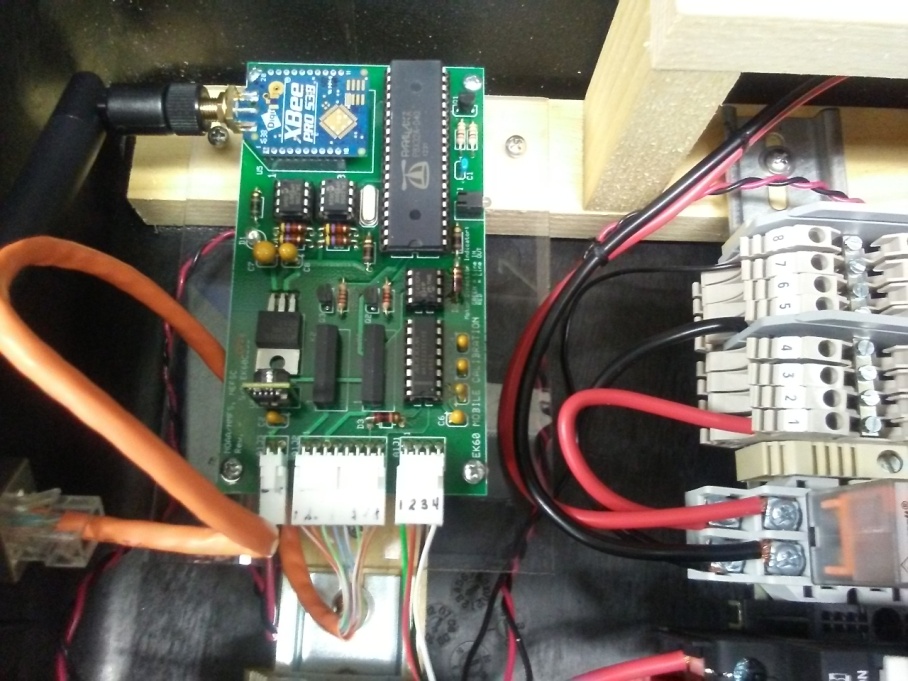
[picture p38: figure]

Figure 2: PCB Serial Header Location.

- Connect the ECHOCAL-10500 AC Power cable to the control box, and plug into a standard AC outlet. Verify that the Red LED light illuminates on the PCB. If not, check that the AC circuit breakers inside the control box are in the ON position.

(Warning: 115 VAC power is applied to the control box at this time. Use caution when handling components inside the control box.)

- Install the Propeller Tool IDE on the PC as per manufacturer’s instructions. Double click on the Propeller Desktop Icon to launch the software.
- The main Propeller Tool window will open. Select File/Open menu item to access the “Open” dialog window. Browse to the latest folder location of the EchoCAL firmware (…/EchoCAL_firmware_v1.2) and open file “EchoCAL.spin”.

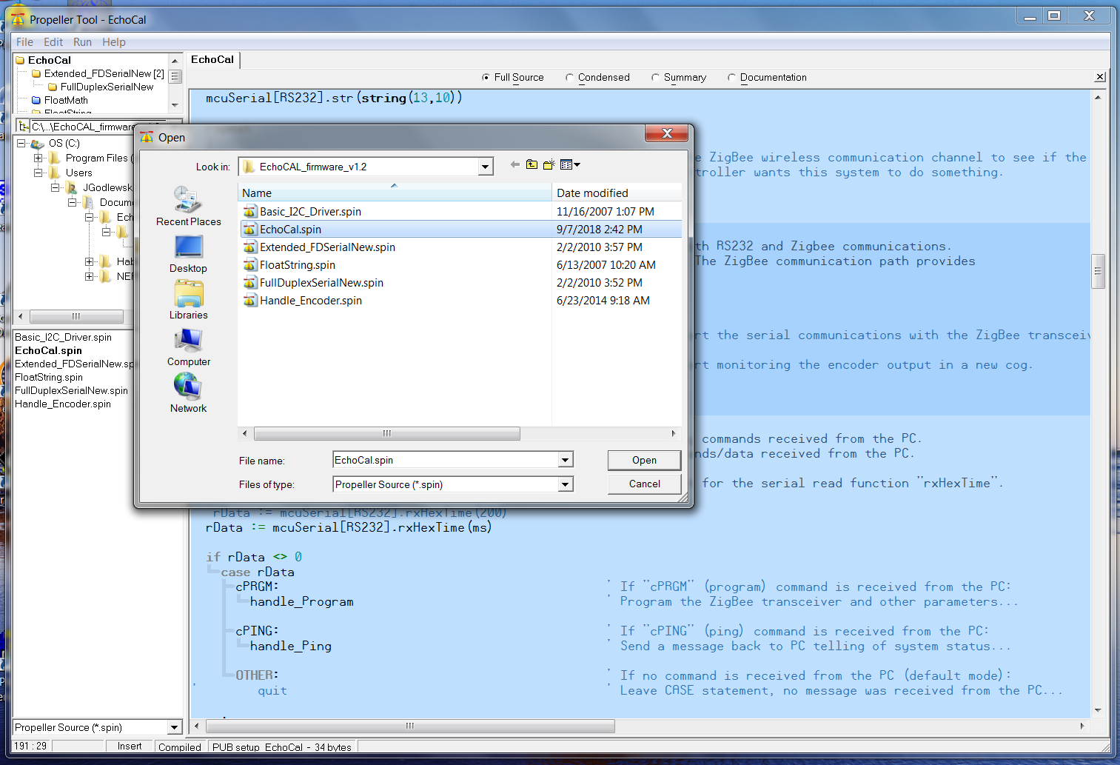
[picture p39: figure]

- Select the Run->Compile Current->Load EEPROM menu item to install the firmware.

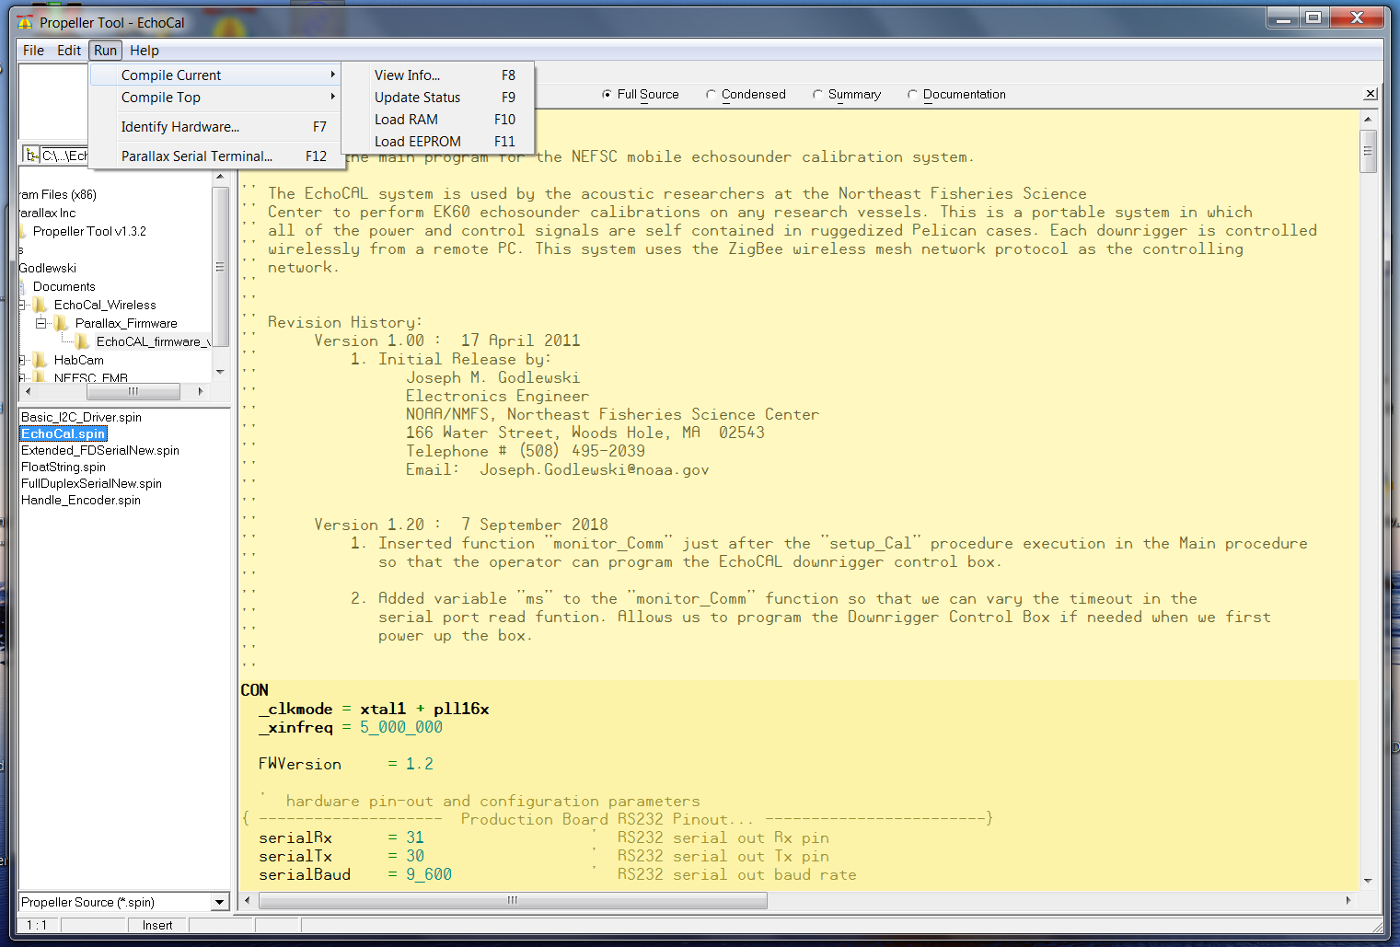
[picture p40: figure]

- At this point, the firmware will be loaded in the EEPROM on the PCB. Proceed to the next section to program the EchoCAL Control Box serial number.

# 3.0 Programming the EchoCAL Control Box Serial Number:

- If power is applied to the EchoCAL Control Box, remove power from the device by either unplugging the power cord, or switch the AC circuit breakers to the OFF position.
- Connect the EchoCAL-10550 Programming Cable from the serial header on the EchoCAL Control Box PCB to a spare COM port on any Window’s based PC. (Note: If no COM ports are available, you can use a USB to Serial adapter cable instead.)
- Launch the Parallax Serial Terminal (https://www.parallax.com/downloads/parallax-serial-terminal) application on the Window’s PC, and open the COM port that EchoCAL is attached to. (Serial port parameters should be set to: Baud Rate = 9600 baud, Data Bits = 8 bits, Parity = None, Stop Bits = 1, Flow Control = None.)
- Apply power to the EchoCAL Control box and verify that the LED on the PCB is illuminated. (Note: When power is first applied to the PCB, the firmware will slave to the RS232 serial port to wait for programming commands from the user’s PC. The user will have 10 seconds to put the microcontroller into “Programming” mode. After 10 seconds, the microcontroller will start its regular firmware routines.)
- Type the character “a” without quotes, and press the return key. You should see a menu similar to the following:

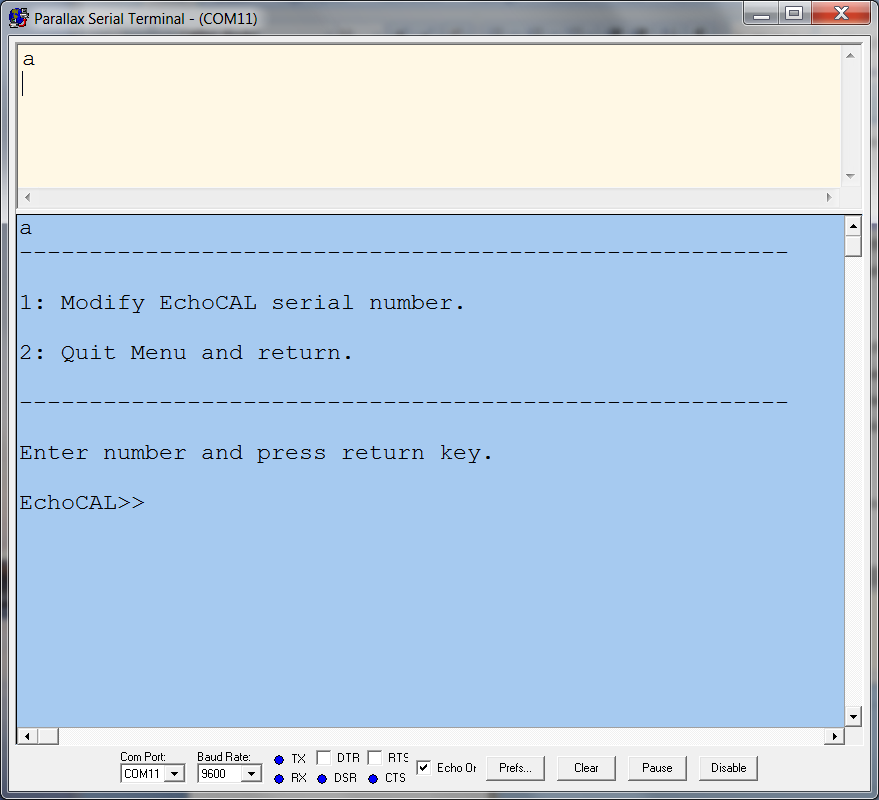
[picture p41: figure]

- Select menu item “1” and press the return key. A new menu should be displayed allowing the user to change the EchoCAL Control Box serial number.

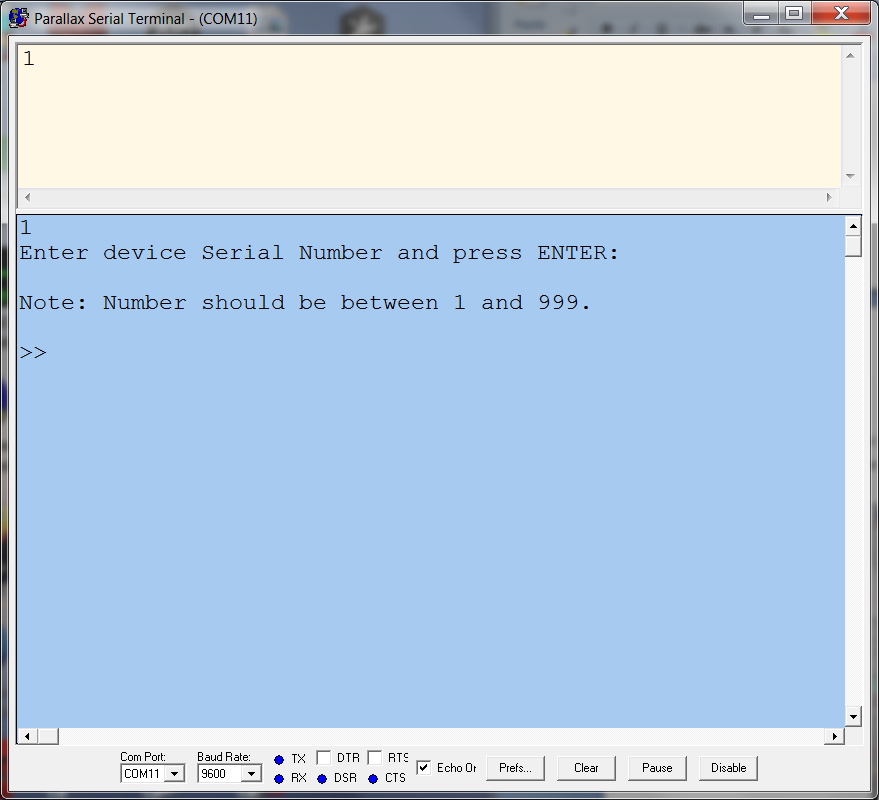
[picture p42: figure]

- Enter the serial number for the control box. The integer number should be from 1 to 999. Press return key to continue. (Notice that the serial number will be prefaced with the characters “EK60C”. The EchoCAL Graphical User Interface (GUI) uses this serial number representation to determine which downrigger to talk to. This step will also change the Node ID of the ZigBee Pro wireless transceiver to the same serial number as the control box.)

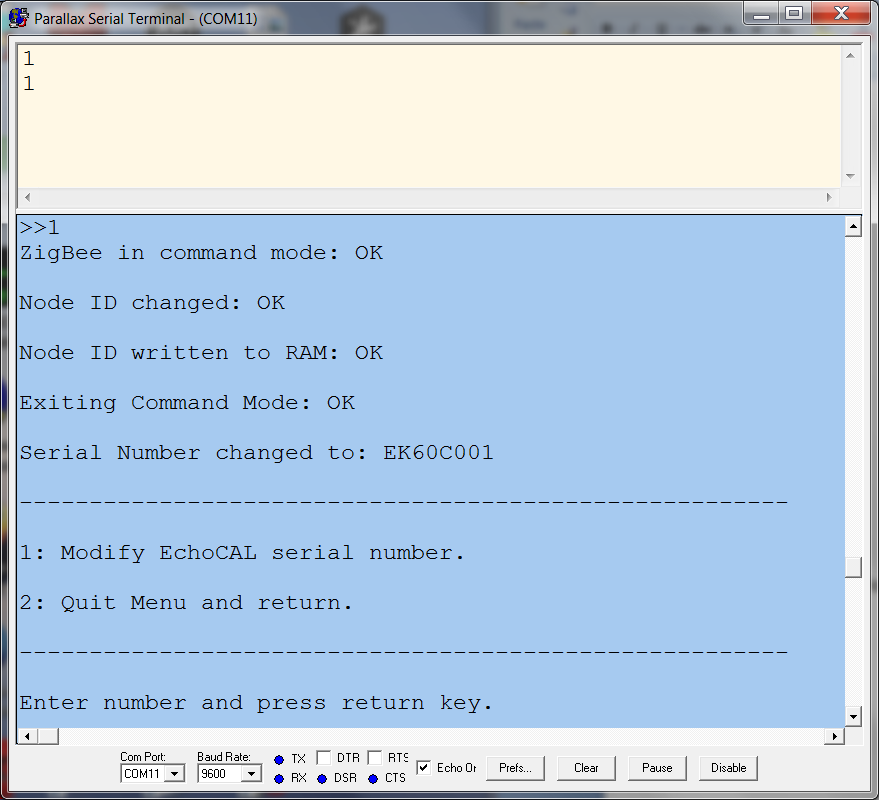
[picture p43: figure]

- Once the serial number has been changed, select menu item “2” to exit the Modify Serial Number menu. The control box’s serial number should now be changed. At this point, the EchoCAL Control Box should be ready for echosounder calibration activities.

NOAA, NMFS, Northeast Fisheries Science Center 166 Water Street Woods Hole, MA 02543

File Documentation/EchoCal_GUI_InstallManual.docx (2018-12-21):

NEFSC Echosounder Calibration System

(EchoCAL)

GUI Software Installation Manual


# 1.0 Introduction:

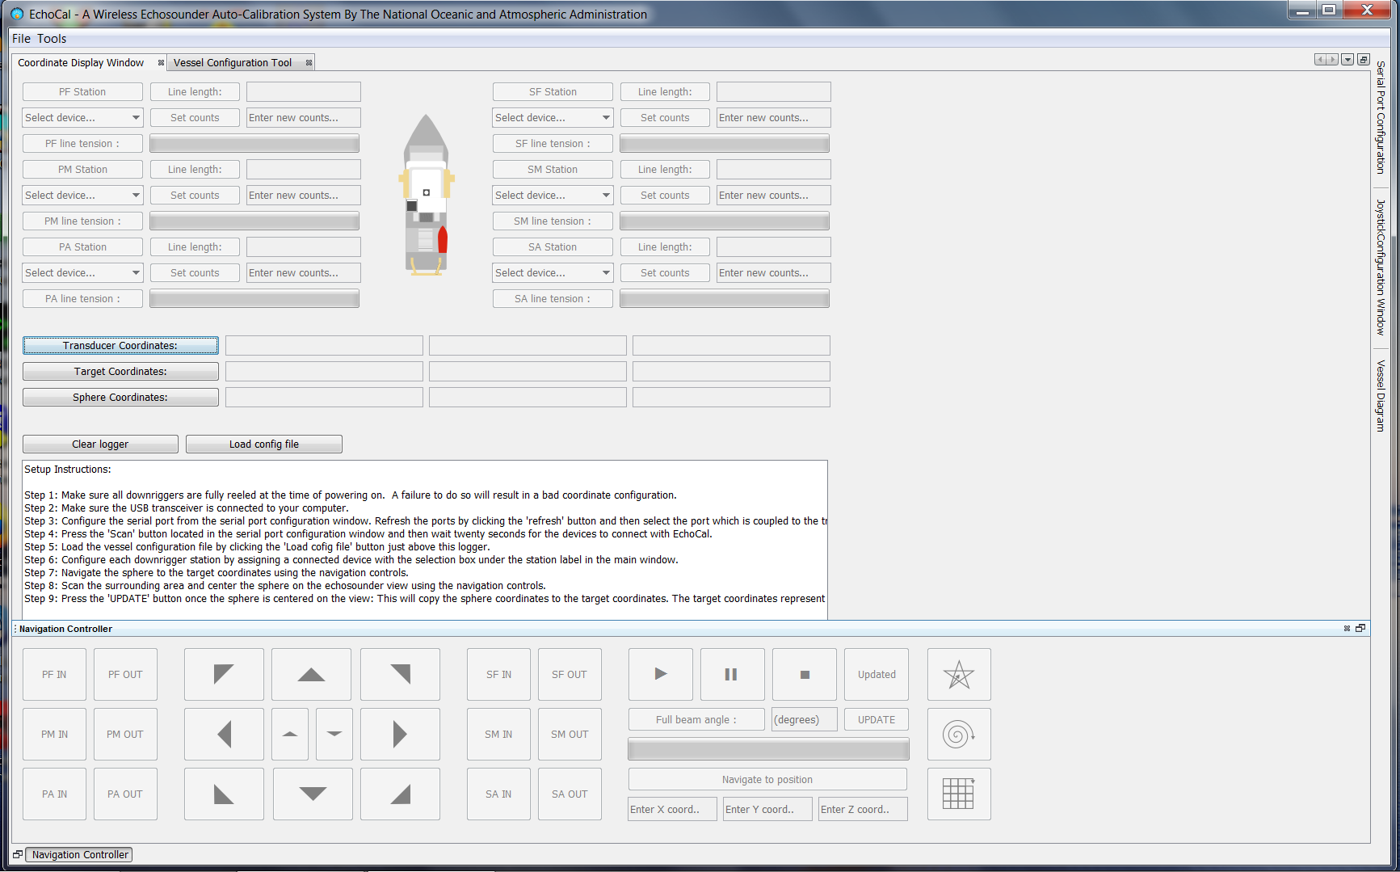
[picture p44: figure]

Figure 1. EchoCAL Graphical User Interface (GUI)

The EchoCAL Graphical User Interface (GUI) provides the software interface which controls the system of powered downriggers for echosounder calibrations. This GUI can be installed on any 64-bit Linux or Windows based PCs in three different ways. The first method is by downloading the executable binary files that are installed in the “bin” folder on the EchoCAL GitHub site.
(https://github.com/jmgodlewski/EchoCAL)
See Section 2 of this manual on how to install EchoCAL from binaries.

The second method is to download all of the EchoCAL GUI JAVA project files and open them in the Netbeans Integrated Development Environment (IDE) (https://netbeans.org/). These project files are located in the “EchoCAL_GUI_Source/EchoCal_Ver1.2” folder on the EchoCAL GitHub site. See Section 3 of this manual on how to load the project files into the Netbeans IDE and run the EchoCAL application.

The user can also create the EchoCAL executable binaries using the EchoCAL GUI project files. This will come in handy if the user needs to fix problems or add features to the code at a later date. See Section 4 of this manual for instructions on creating a packaged executable distribution of the EchoCAL software.

# 2.0 Installing EchoCAL Graphical User Interface (GUI) from binaries:

Installing EchoCAL using the binaries developed for this system is the easiest and quickest method of testing the hardware and conducting echosounder calibrations. The EchoCAL application contains a copy of the JAVA Runtime Environment (JRE) embedded with the application. The user can run EchoCAL on any PC, even if a version of JAVA is not installed on that machine. To install EchoCAL, perform the following steps:

1. Download the EchoCAL executable files from the EchoCAL GitHub web site depending on which operating system that the researcher is using. For example, if a researcher is using a Windows 64-bit Operating System, download the EchoCAL files from the “bin/Win64” folder on the GitHub site.
  a. Navigate to the EchoCAL GitHub site (https://github.com/jmgodlewski/EchoCAL) using any web browser, and select the “bin/Win64” folder. (See Figure 2.)

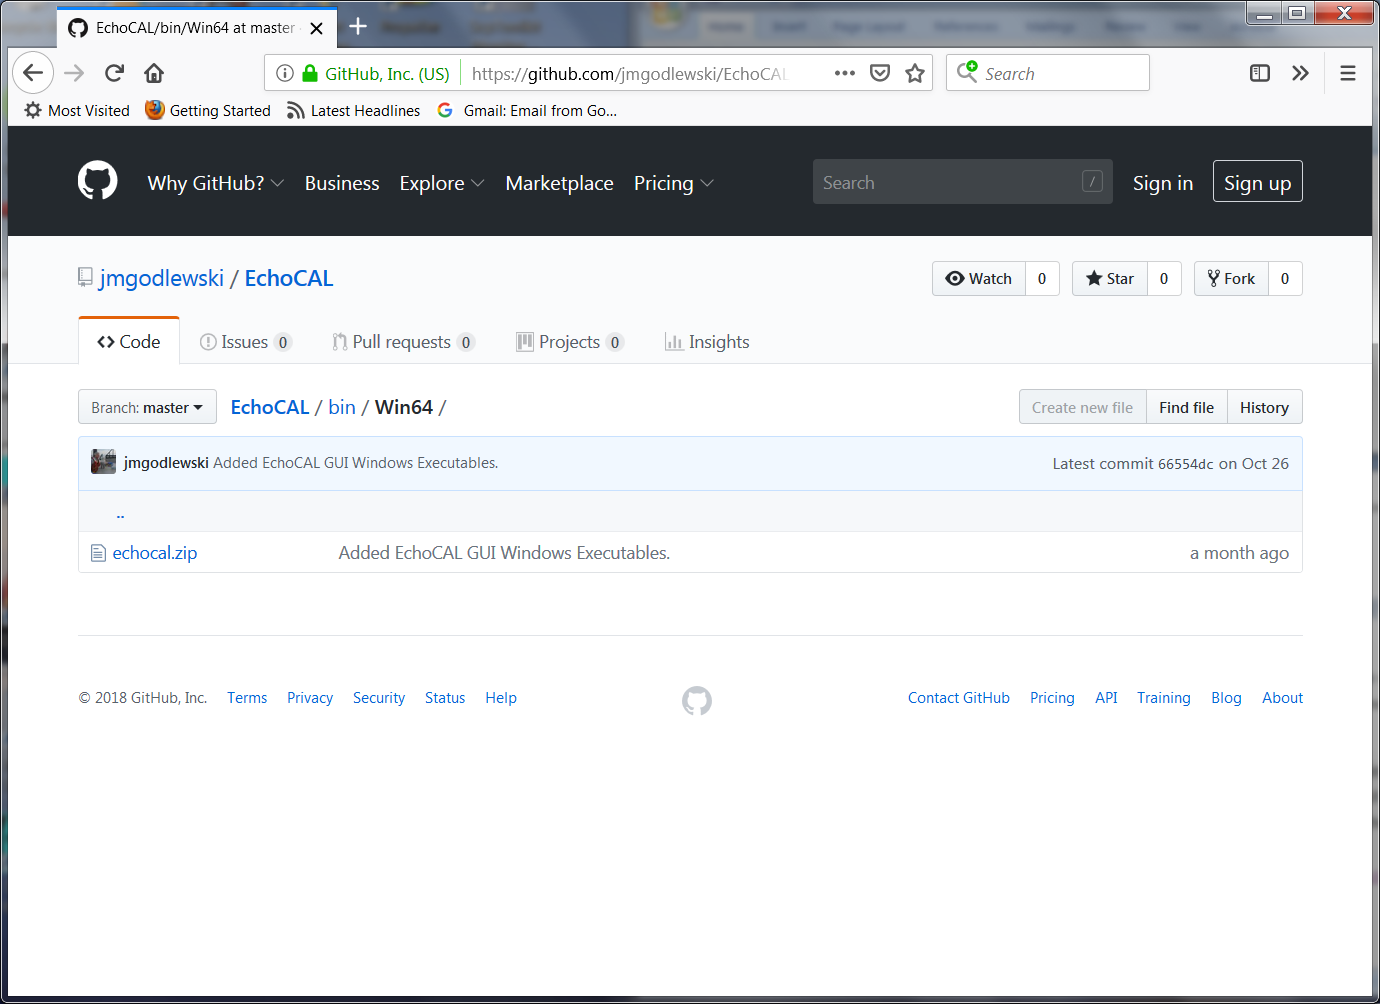
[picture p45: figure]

Click on echocal.zip.

Figure 2. EchoCAL GitHub Site: /bin/Win64 Folder.

  b. Click on the “echocal.zip” file in the web browser’s window. A new page will open which will allow you to download the “echocal.zip” file. Select the Download button to download the ZIP file to your PC. (See Figure 3.)

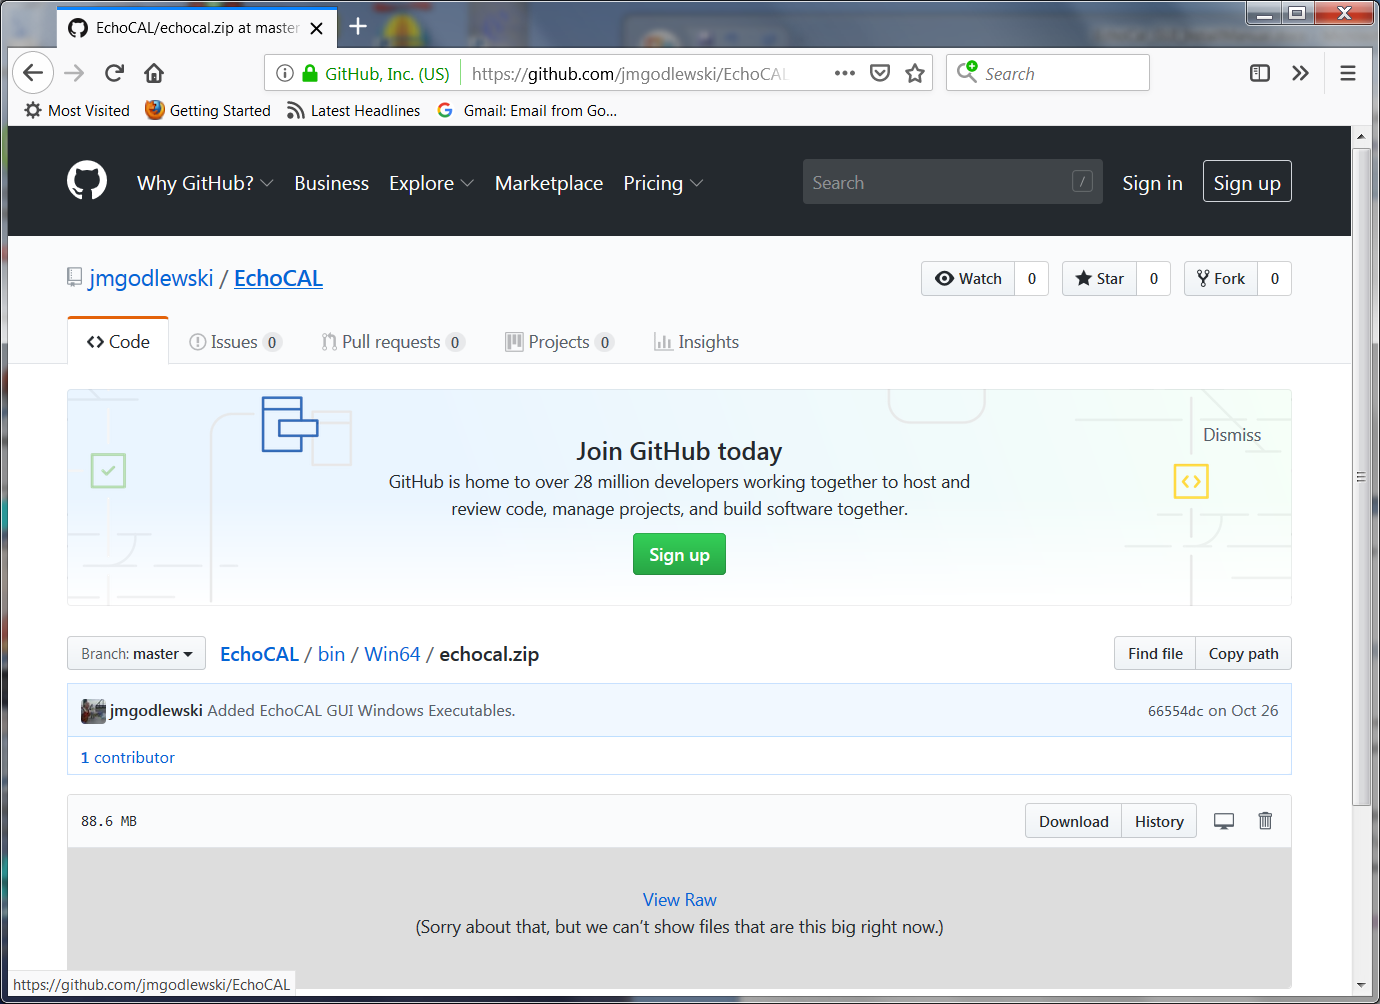
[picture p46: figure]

Figure 3. Download "echocal.zip" file from GitHub.

Click Download button.

  c. When the ZIP file finishes downloading to your PC, navigate to the Downloads folder and extract the “echocal.zip” file to a local folder that the user has write privileges to. (See Figure 4 for ZIP file contents.)

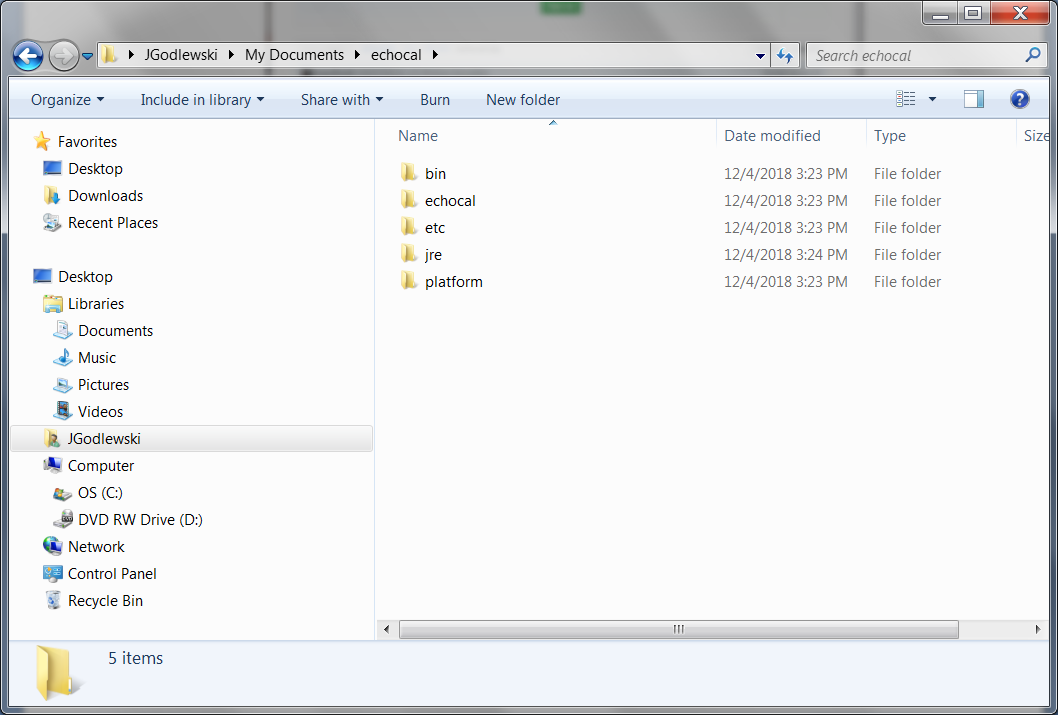
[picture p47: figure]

Figure 4. Unzipped EchoCAL folder.

  d. Navigate to the “bin” folder and double-click on the “echocal64” executable to launch the EchoCAL GUI application. (See Figure 5.) Note: For the Linux version of the software, there will be a shell script called “echocal”. Make sure this script is set with proper run permissions on the Linux PC, and double-click the icon to launch the EchoCAL GUI.

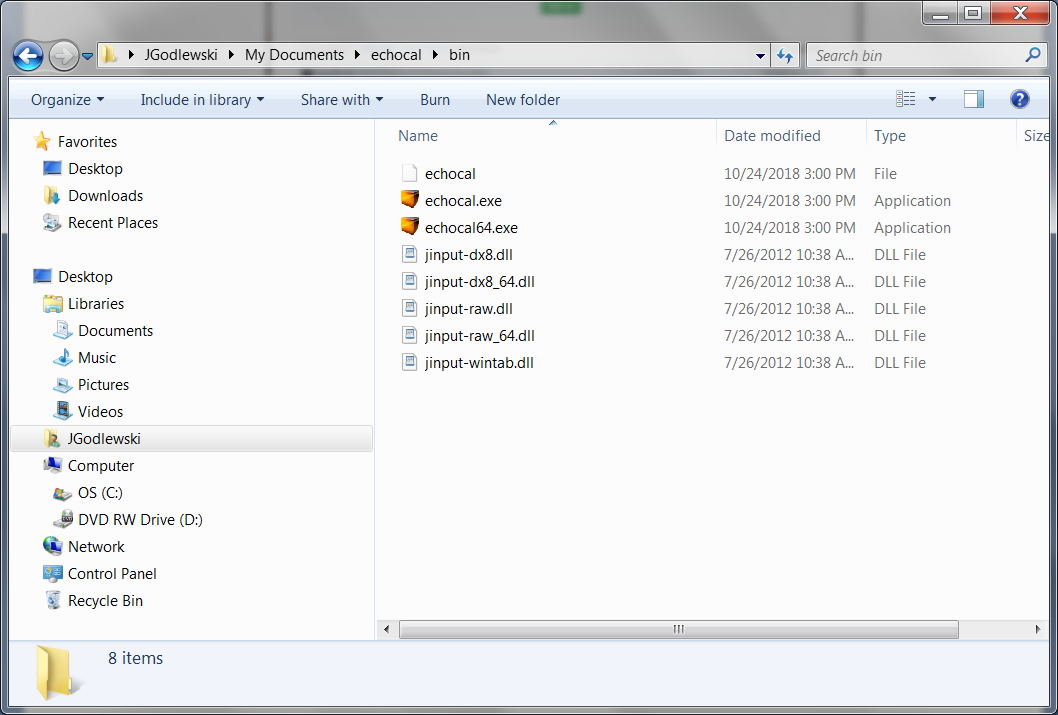
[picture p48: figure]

Double-click echocal64.exe to
launch the EchoCAL GUI app.

Figure 5. EchoCAL Bin folder.

2. See the EchoCAL Users Manual for information on how to use the software.

# 3.0 Installing EchoCAL Graphical User Interface (GUI) from source code:

The EchoCAL Graphical User Interface (GUI) is a JAVA based application which was developed using the Netbeans IDE 8.1 (https://netbeans.org) and JAVA JDK 1.8 (64 bit) from Oracle (https://www.oracle.com/technetwork/java/javase/downloads/index.html). Prior to downloading the EchoCAL source files, install both the latest Netbeans IDE and the JAVA JDK to your PC according to developers’ instructions. Once the JAVA development environment is installed, perform the following steps to setup the EchoCAL project:

1. Download the complete EchoCAL project from the EchoCAL GitHub site (https://github.com/jmgodlewski/EchoCAL) by clicking on the green “Clone or download” button in the main EchoCAL GitHub window. (See Figure 6.)

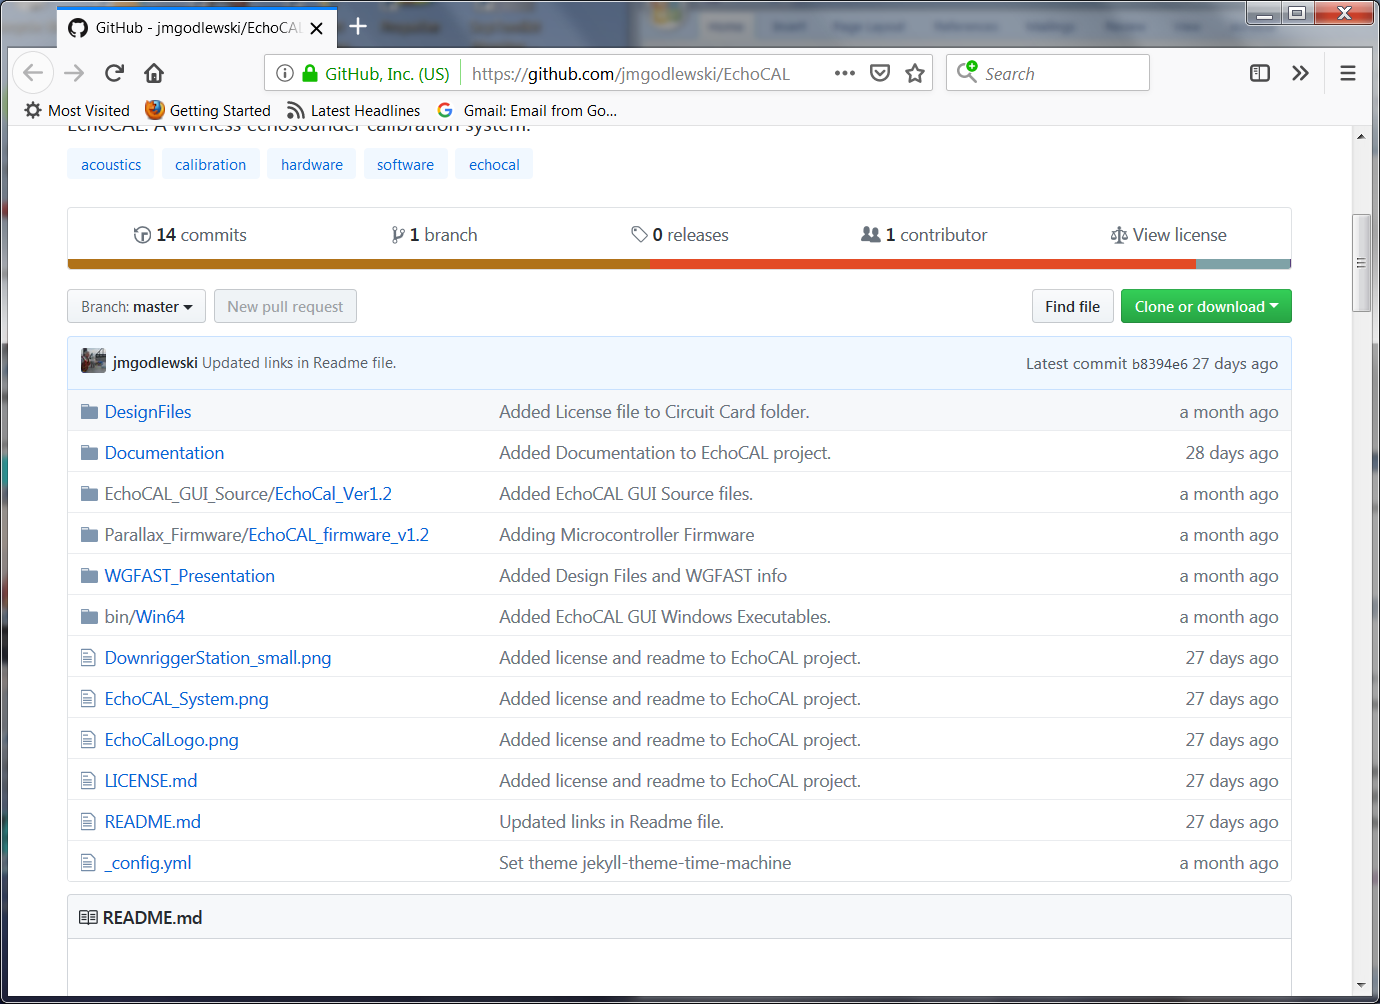
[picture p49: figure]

Figure 6. EchoCAL main GitHub project folder.

2. Select the “Download ZIP” option to download a ZIP archive of the complete EchoCAL project. Extract all files from the “EchoCAL-master” ZIP archive to a folder that the user has read/write access to.
3. The EchoCAL GUI application uses a third party module called RXTX, which provides an interface to the serial ports of a PC. Libraries for RXTX must be copied into the local JAVA JDK folder so that the GUI application can make use of the RXTX serial port modules. This can be done by performing the following steps:
  a. Navigate to the folder “EchoCAL-master/EchoCAL_GUI_Source/EchoCAL_Ver1.2/EchoCalCustonFiles”. (See Figure 7.)

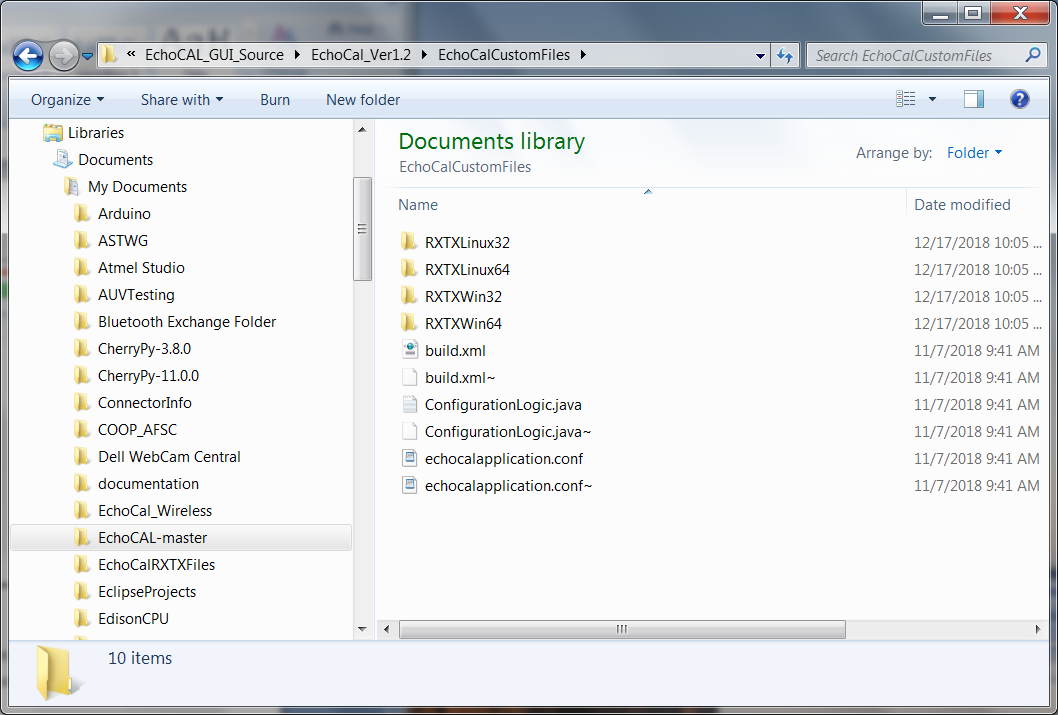
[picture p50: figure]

Figure 7. “EchoCalCustomFiles” folder contents.

  b. This folder contains RXTX modules for the Linux and Windows operating systems, both 32- and 64-bit versions. Select the version that will work for your current operating system. For a Windows 64-bit OS, open the RXTXWin64 folder to access the RXTX modules for that operating system. (See Figure 8.)

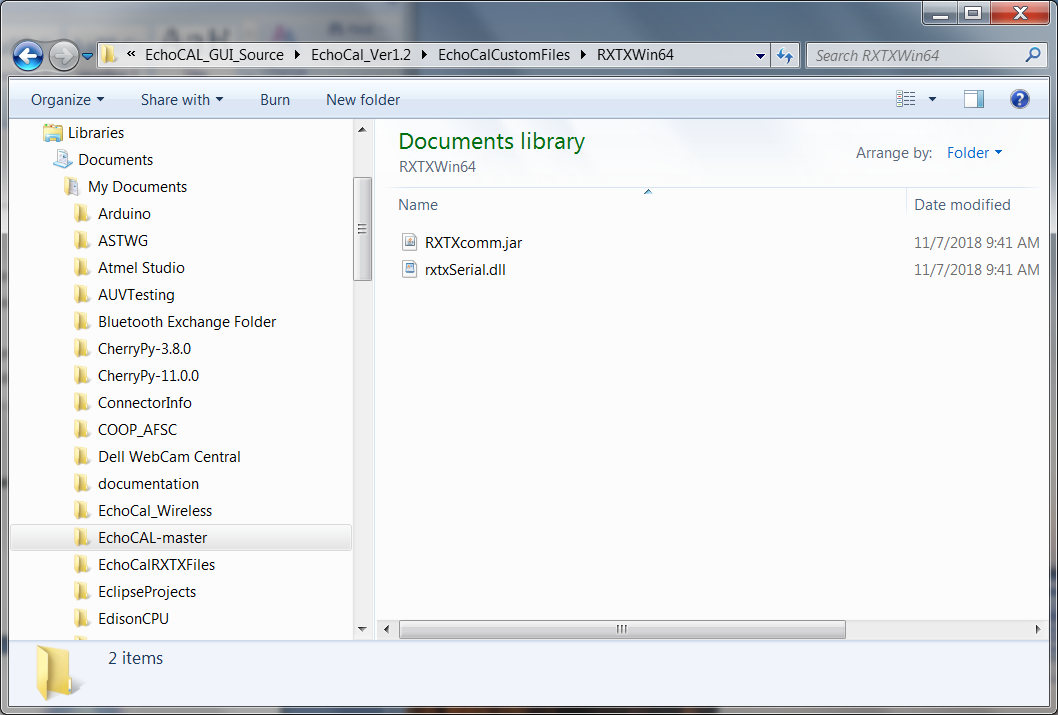
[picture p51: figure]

Figure 8. "RXTXWin64" folder contents.

  c. Copy the “rxtxSerial.dll” file to the PCs local JAVA JDK folder. For example, the file should be copied to “C:/ProgramFiles/Java/jdk1.8.0_101/jre/bin” for Windows JAVA JDK version 1.8.0.101. (See Figure 9.)

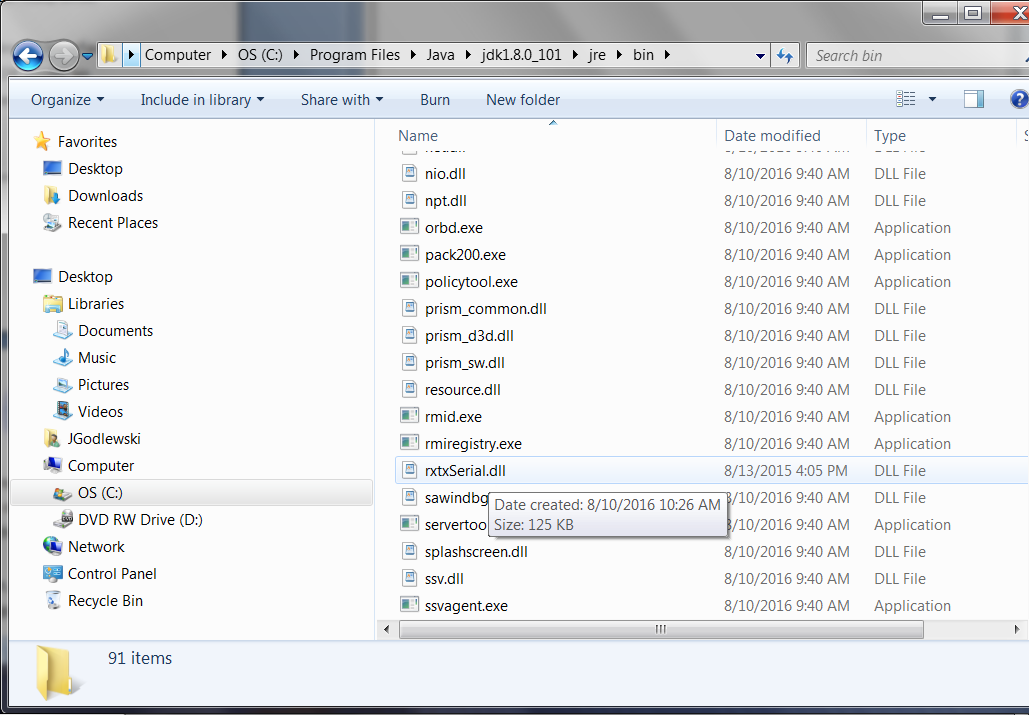
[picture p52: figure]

Figure 9. Local JAVA JDK folder for rxtxSerial.dll file.

  d. Copy the “RXTXcomm.jar” file to the “C:/ProgramFiles/Java/jdk1.8.0_101/jre/lib/ext” folder. (See Figure 10.)

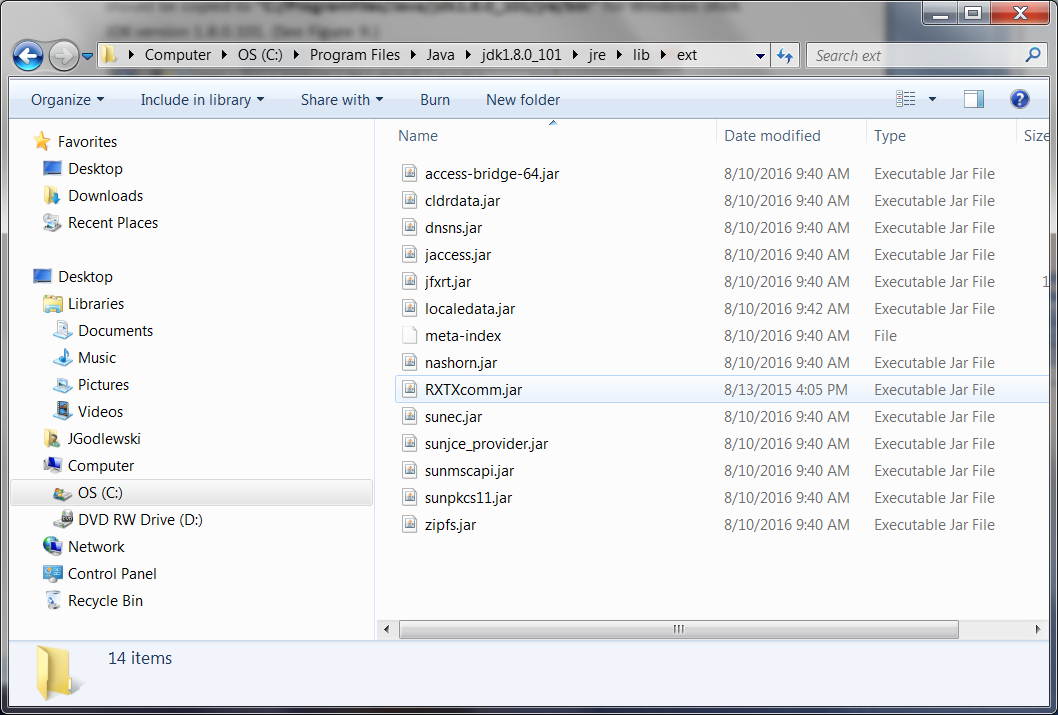
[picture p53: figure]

Figure 10. Local JAVA JDK folder for RXTXcomm.jar file.

4. Launch the Netbeans IDE. From the main Netbeans IDE window, select “File/Open Project” menu item to open the EchoCAL GUI project. (See Figure 11.)

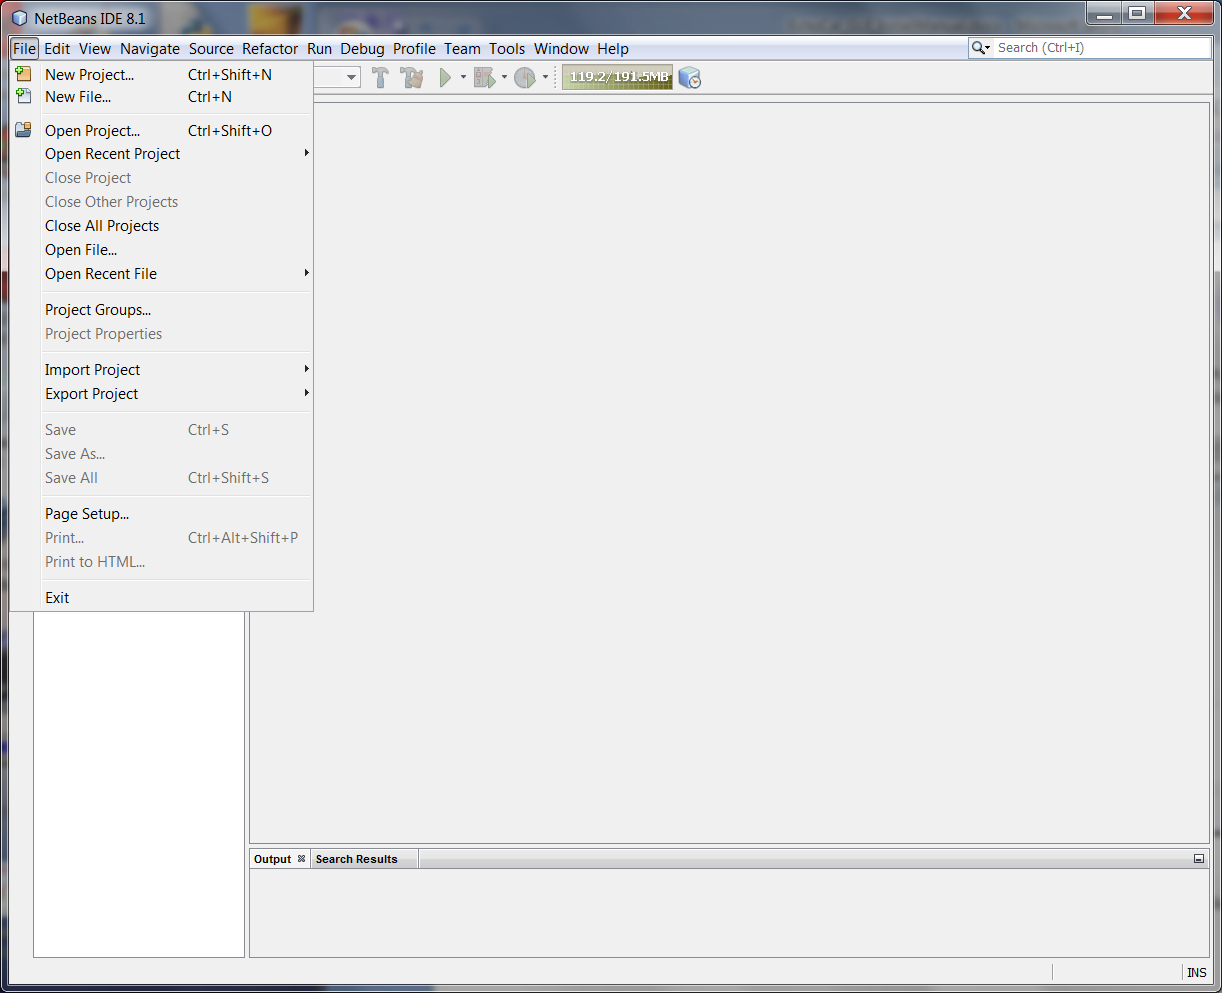
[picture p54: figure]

Open Project menu item.

Figure 11. Open Project menu item.

5. The Open Project dialog box will open. Browse to the “EchoCAL-master/EchoCAL_GUI_Source” folder and select the “EchoCal_Ver1.2” project. (See Figure 12.)

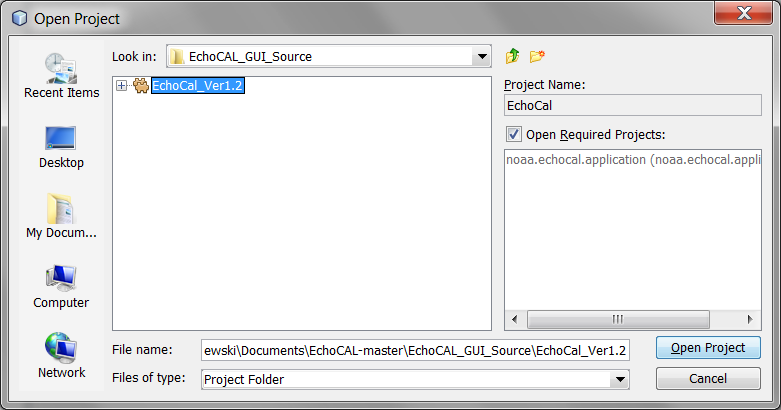
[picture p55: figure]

Figure 12. Open Project Dialog Box.

6. Click on the Open Project button. The EchoCAL GUI project will open in the main Netbeans window. (See Figure 13.)

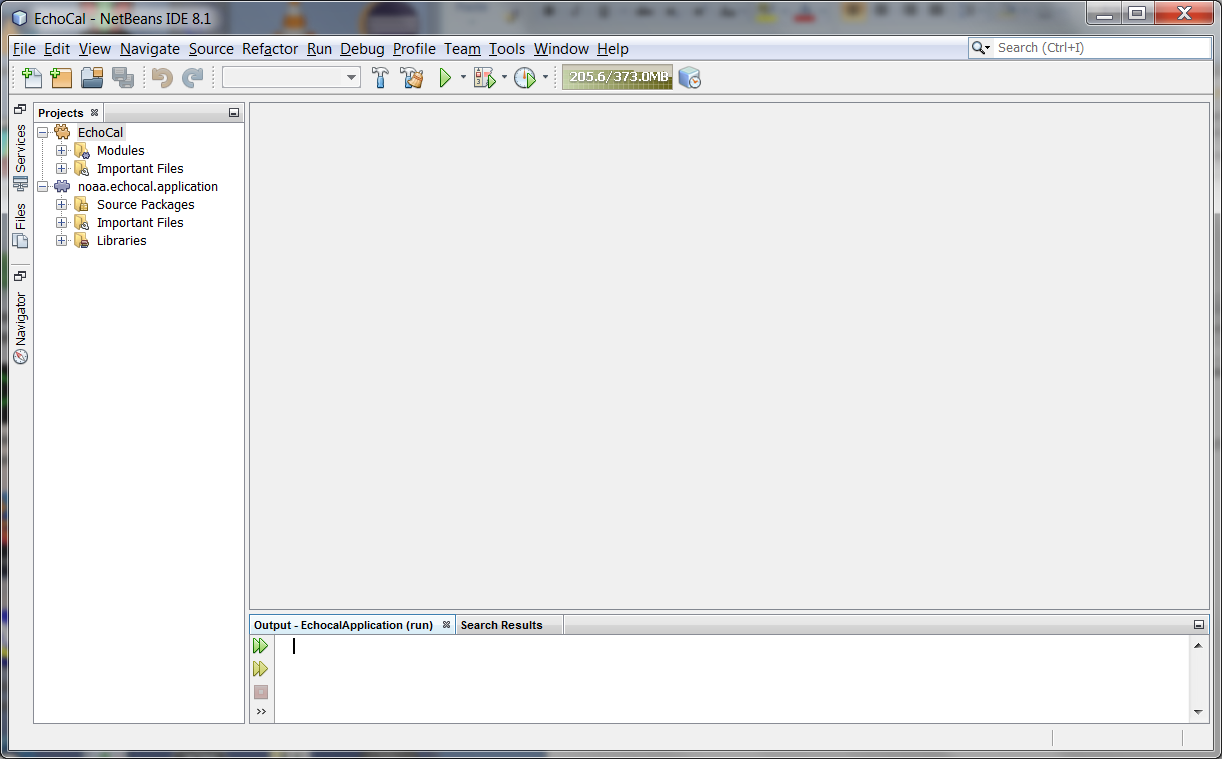
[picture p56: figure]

Clean & Build button.

Run Project button.

Figure 13. EchoCAL Project Main Window.

7. Select the “Clean and Build Project” button in the toolbar to compile and clean the project. To run the application, select the “Run Project” toolbar button. (See Figure 13.) This will launch the EchoCAL GUI application.
8. See the EchoCAL Users Manual for details on using the EchoCAL software.

# 4.0 Creating EchoCAL executable from EchoCAL Graphical User Interface (GUI) source code:

The Netbeans Integrated Development Environment (IDE) can create executable packages that the user can run independent of the Netbeans IDE. The EchoCAL GUI application should be packaged as a “ZIP” distribution so that the software can be ported to other PCs that do not have the Netbeans IDE or JAVA installed. To create the EchoCAL GUI application, perform the following steps:

1. Make all software changes and test the application as shown in Section 3 of this document.
2. In the main Netbeans Project window, right-click on the EchoCal module in the Projects tab portion of the main window and select Package as/ZIP Distribution. (See Figure 14.)

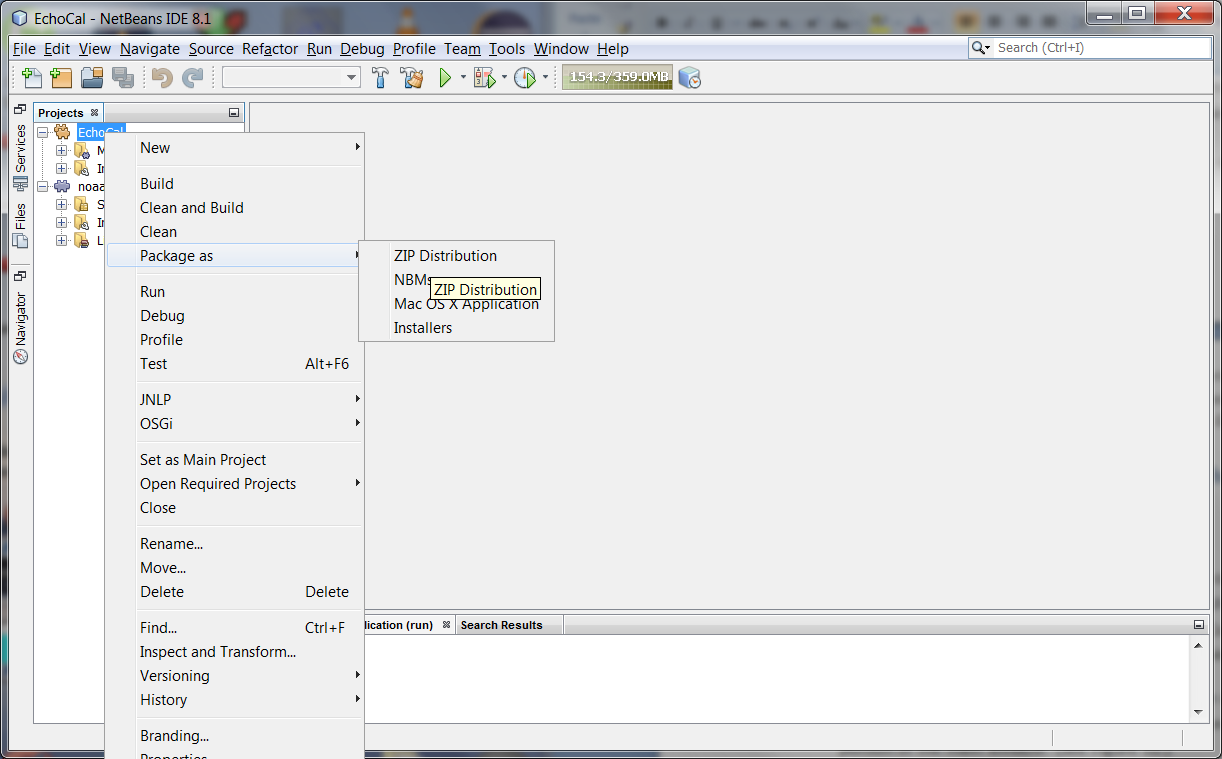
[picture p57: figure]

Figure 14. Packaging EchoCAL as a ZIP distribution.

3. The EchoCAL GUI application will be packaged as a ZIP file which can then be extracted at a later time. At this point, the GUI application does not have a JAVA Runtime Environment (JRE) packaged with it. It is a good idea to package the JRE with the application so that it can be installed on user PCs without the need to install a separate JAVA JRE on the PC. To add the JRE to the ZIP package, assuming that the developer is using a Windows machine, perform the following steps: (Note: Steps should be similar in a Linux OS as well.)
  a. In Windows Explorer, navigate to the Java Development kit (JDK) that was used to develop the application. In this example, navigate to the “C:/ProgramFiles/Java/jdk1.8.0_101/” (See Figure 15.)

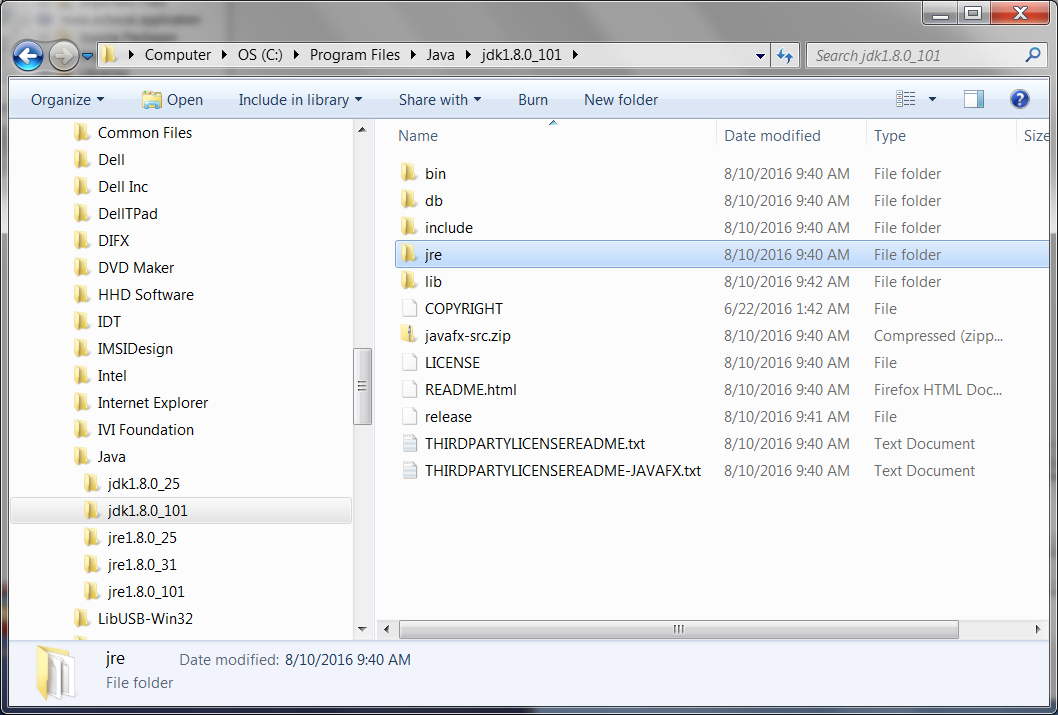
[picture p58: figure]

Figure 15. Java Development Kit (JDK) Folder.

  b. Right-Click on the “jre” folder and select “Copy”.
  c. Navigate back to the “EchoCAL-master/EchoCAL_GUI_Source/EchoCAL_Ver1.2/” project folder. When Netbeans created the ZIP distribution of the EchoCAL GUI, it created a new “dist” folder in the main project folder. (See Figure 16.) This folder contains the “echocal.zip” application file.

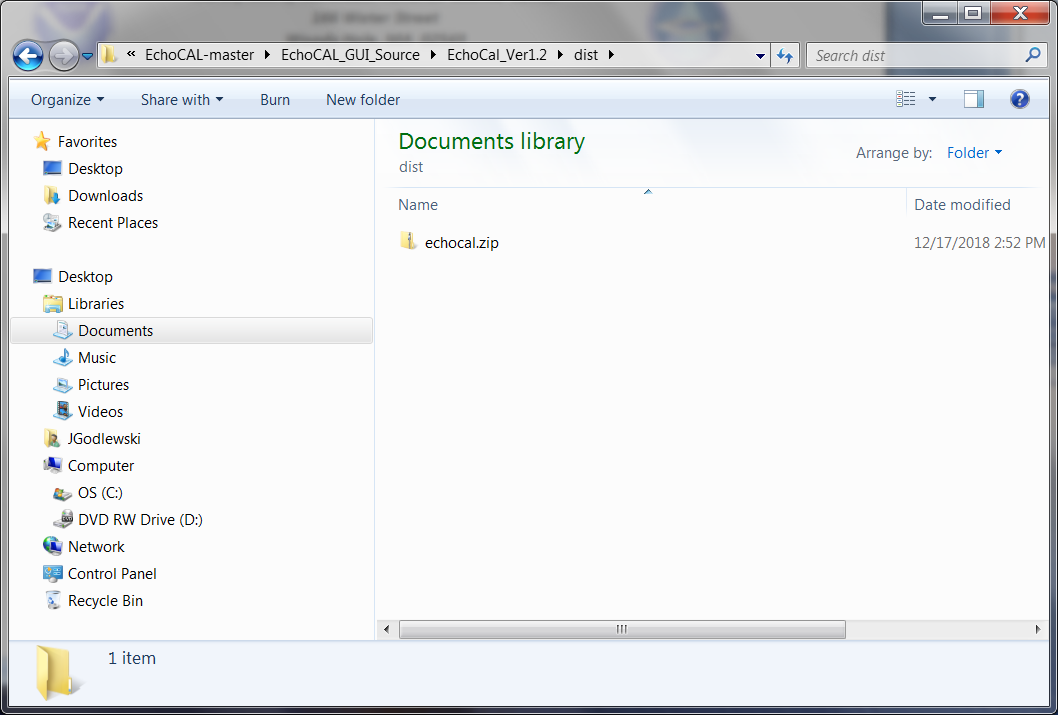
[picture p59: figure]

Figure 16. ZIP Distribution Folder for EchoCAL.

  d. In Windows Explorer, double-click on the “echocal.zip” file to open the ZIP file in an Explorer window. Double-Click on the “echocal” folder to open the application folder. (See Figure 17.)

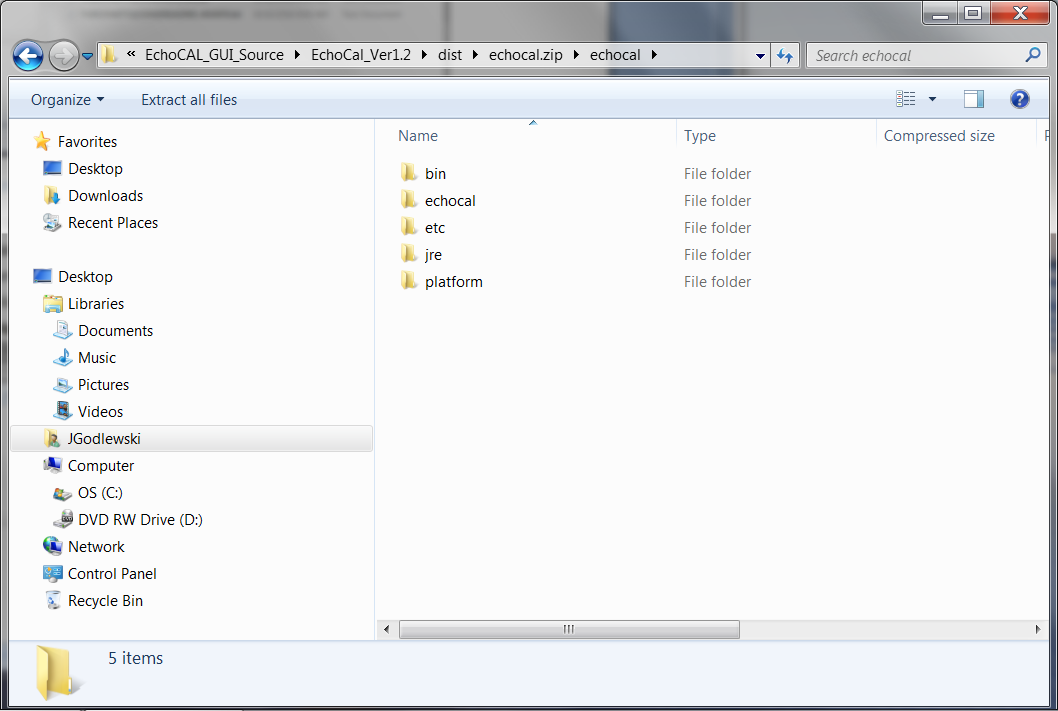
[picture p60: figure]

Figure 17. New JRE folder inside "echocal.zip" file.

  e. Right-Click in this window, and select “Paste” from the contextual menu. The JRE folder will be compressed/copied into the “echocal.zip” distribution file. (See Figure 17).
4. Now that the JAVA Runtime Environment has been copied into the EchoCAL GUI distribution package, we now need to copy the Dynamic Link Libraries (DLLs) for the USB Joystick functionality. Navigate to the “EchoCAL-master/EchoCAL_GUI_Source/EchoCAL_Ver1.2/jinput” folder. Select the following DLLs: jinput-dx8.dll; jinput-dx8_64.dll; jinput-raw.dll; jinput-raw_64.dll; and jinput-wintab.dll. Right-Click on the files, and select “Copy”. (See Figure 18.) (Note: If the ZIP package was developed in Linux, copy the files libjinput-linux.so and libjinput-linux64.so.)

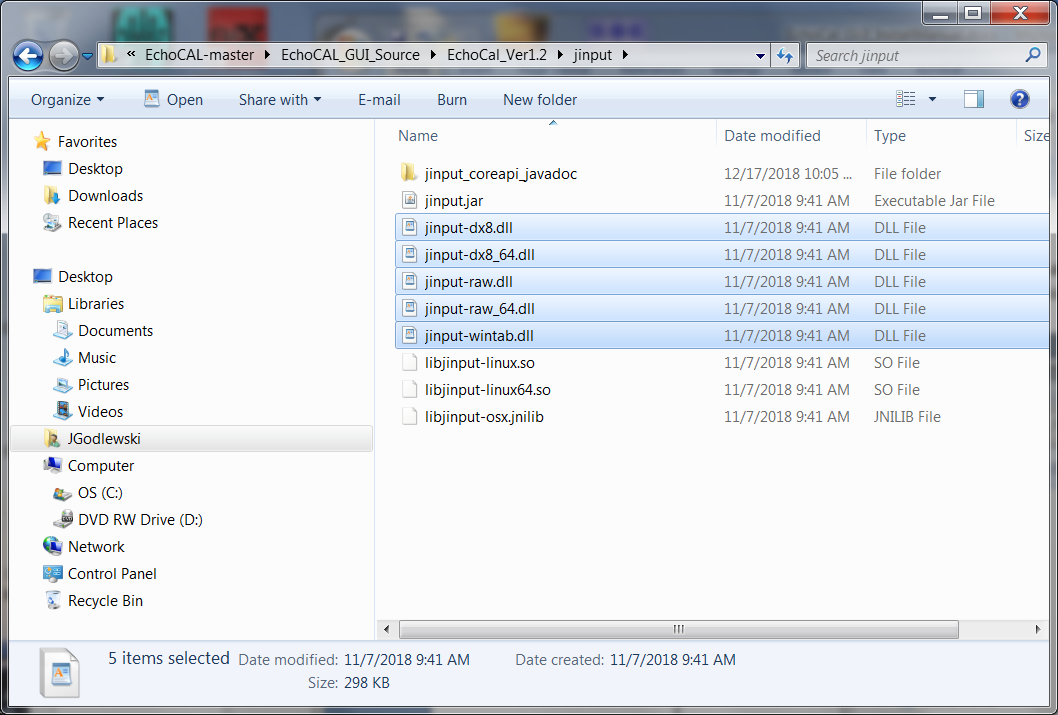
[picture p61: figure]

Figure 18. JInput Dynamic Link Libraries.

5. Next, navigate to the “EchoCAL-master/EchoCAL_GUI_Source/EchoCAL_Ver1.2/dist/echocal.zip/echocal/bin” folder. Right-click in the folder and select “Paste”. This will add the libraries to the EchoCAL executable folder for use by the application. (See Figure 19.)

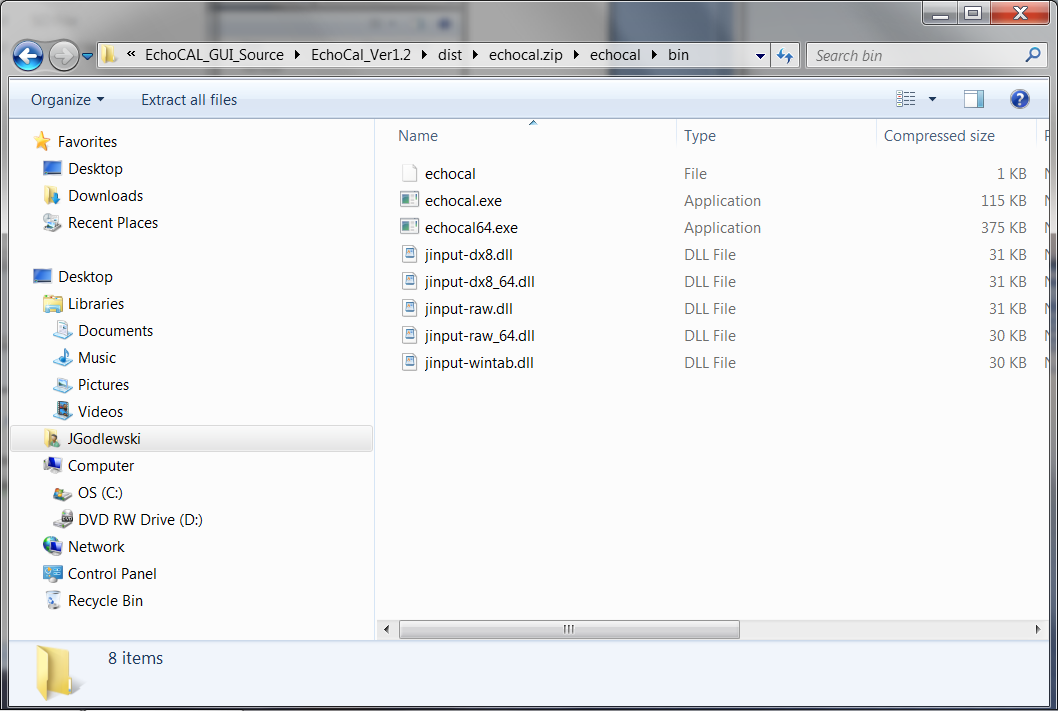
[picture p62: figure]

Figure 19. DLLs copied to ZIP distribution folder.

6. At this point, the EchoCAL ZIP distribution package is ready for deployment.

NOAA, NMFS, Northeast Fisheries Science Center 166 Water Street Woods Hole, MA 02543

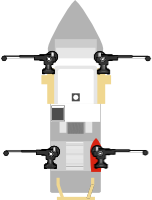
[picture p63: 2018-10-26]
EchoCAL_GUI_Source/EchoCal_Ver1.2/noaa.echocal.application/build/classes/Resources/PFSFSAPAConfigDiagram.png

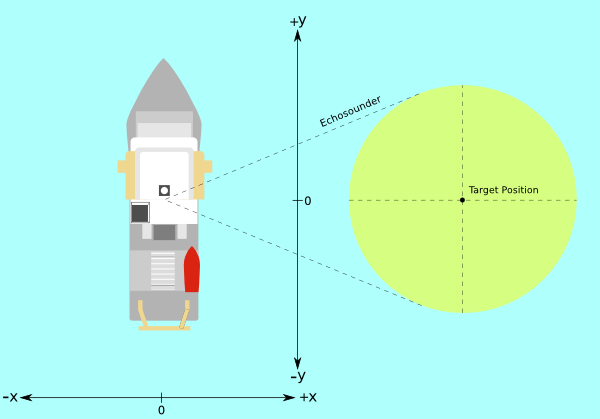
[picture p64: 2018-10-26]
EchoCAL_GUI_Source/EchoCal_Ver1.2/noaa.echocal.application/build/classes/Resources/NoaaVesselTopViewConfigurationGraphic.png

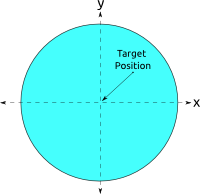
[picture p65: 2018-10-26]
EchoCAL_GUI_Source/EchoCal_Ver1.2/noaa.echocal.application/build/classes/Resources/RadarCrossSectionDiagramGraphic.png

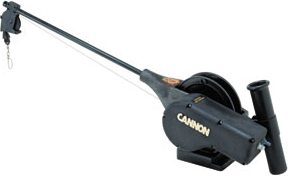
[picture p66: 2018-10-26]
DesignFiles/WiringDiagrams/Cannon_Downrigger_New.png

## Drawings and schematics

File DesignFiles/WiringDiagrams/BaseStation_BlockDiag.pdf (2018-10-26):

D

D

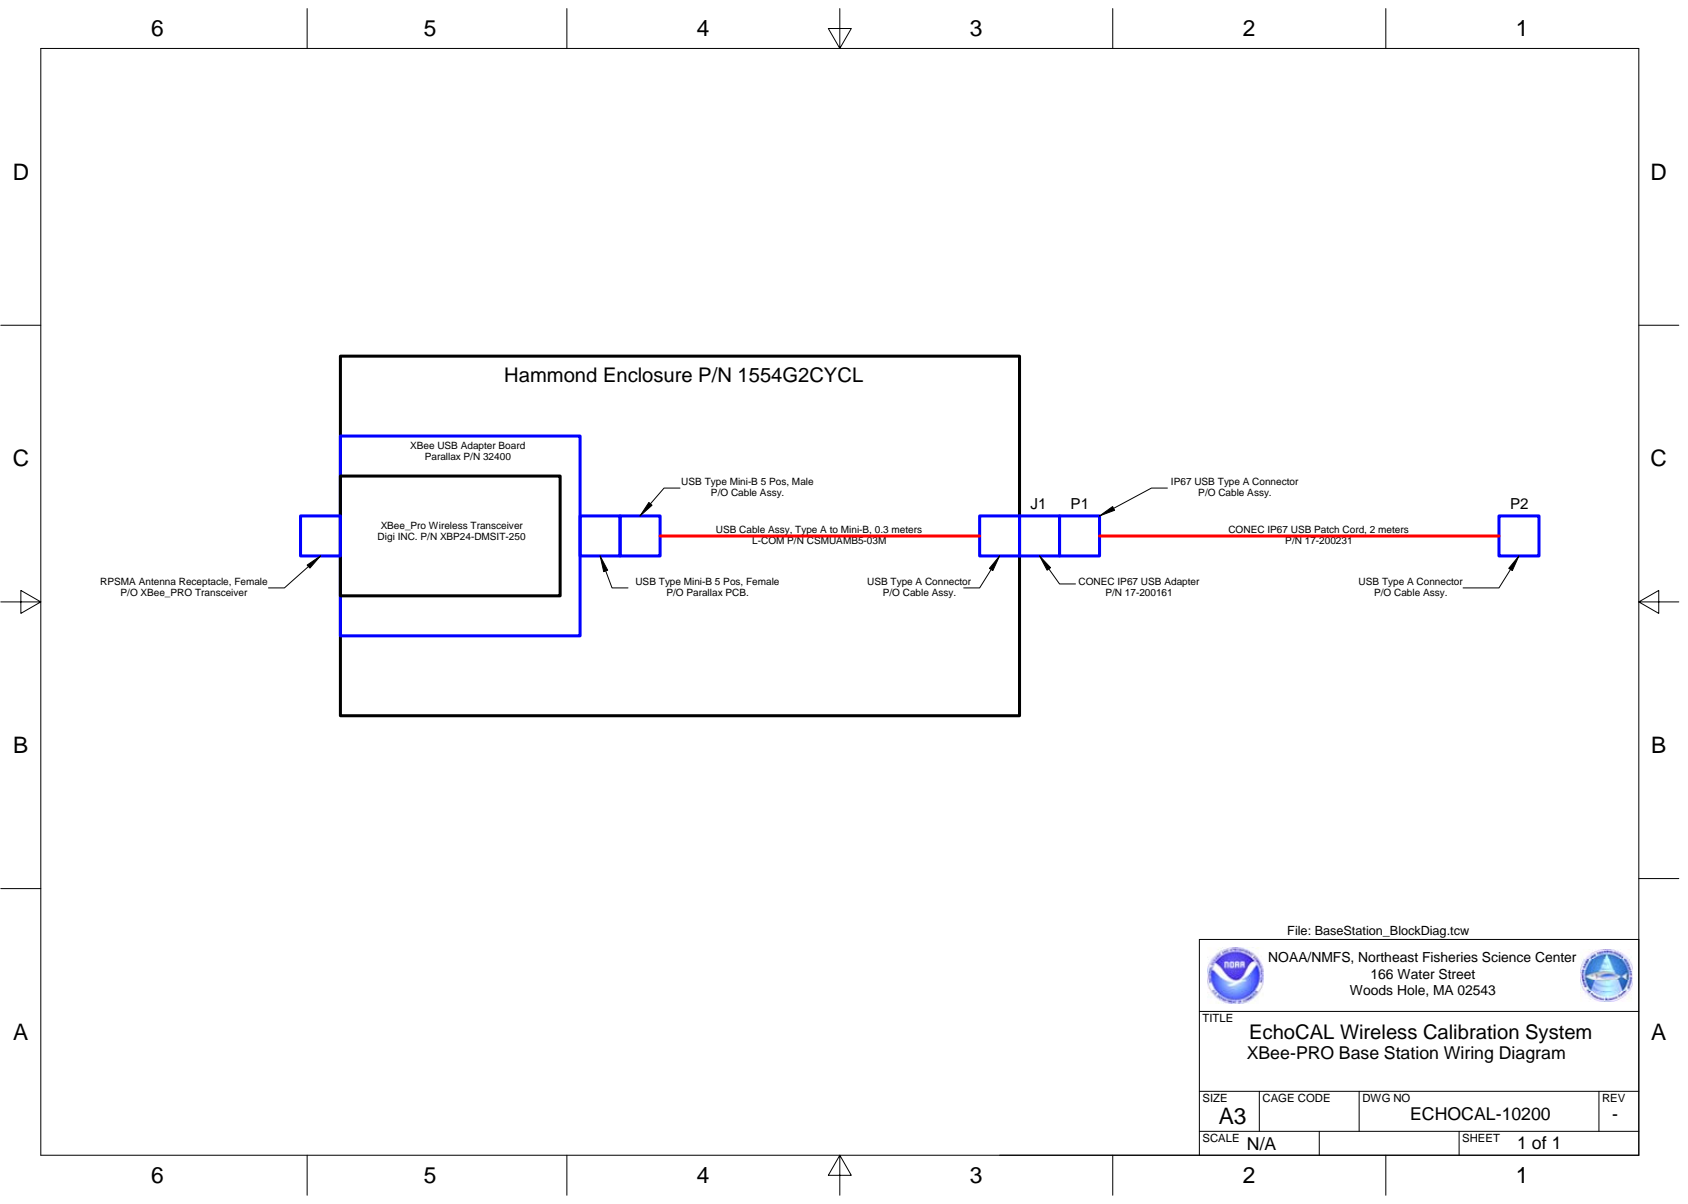
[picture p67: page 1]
Hammond Enclosure P/N 1554G2CYCL; XBee_Pro Wireless Transceiver; Digi INC. P/N XBP24-DMSIT-250; USB Cable Assy, Type A to Mini-B, 0.3 meters L-COM P/N CSMUAMB5-03M

XBee USB Adapter Board
Parallax P/N 32400

USB Type Mini-B 5 Pos, Male
P/O Cable Assy.

IP67 USB Type A Connector

CONEC IP67 USB Patch Cord, 2 meters

RPSMA Antenna Receptacle, Female
P/O XBee_PRO Transceiver

USB Type Mini-B 5 Pos, Female
P/O Parallax PCB.

USB Type A Connector

CONEC IP67 USB Adapter

File: BaseStation_BlockDiag.tcw
NOAA/NMFS, Northeast Fisheries Science Center

166 Water Street
Woods Hole, MA 02543

TITLE
EchoCAL Wireless Calibration System
XBee-PRO Base Station Wiring Diagram

SIZE A3 | CAGE CODE | DWG NO ECHOCAL-10200 | REV -

SCALE N/A | | SHEET

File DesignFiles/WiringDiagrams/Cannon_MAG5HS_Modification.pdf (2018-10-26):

D

D

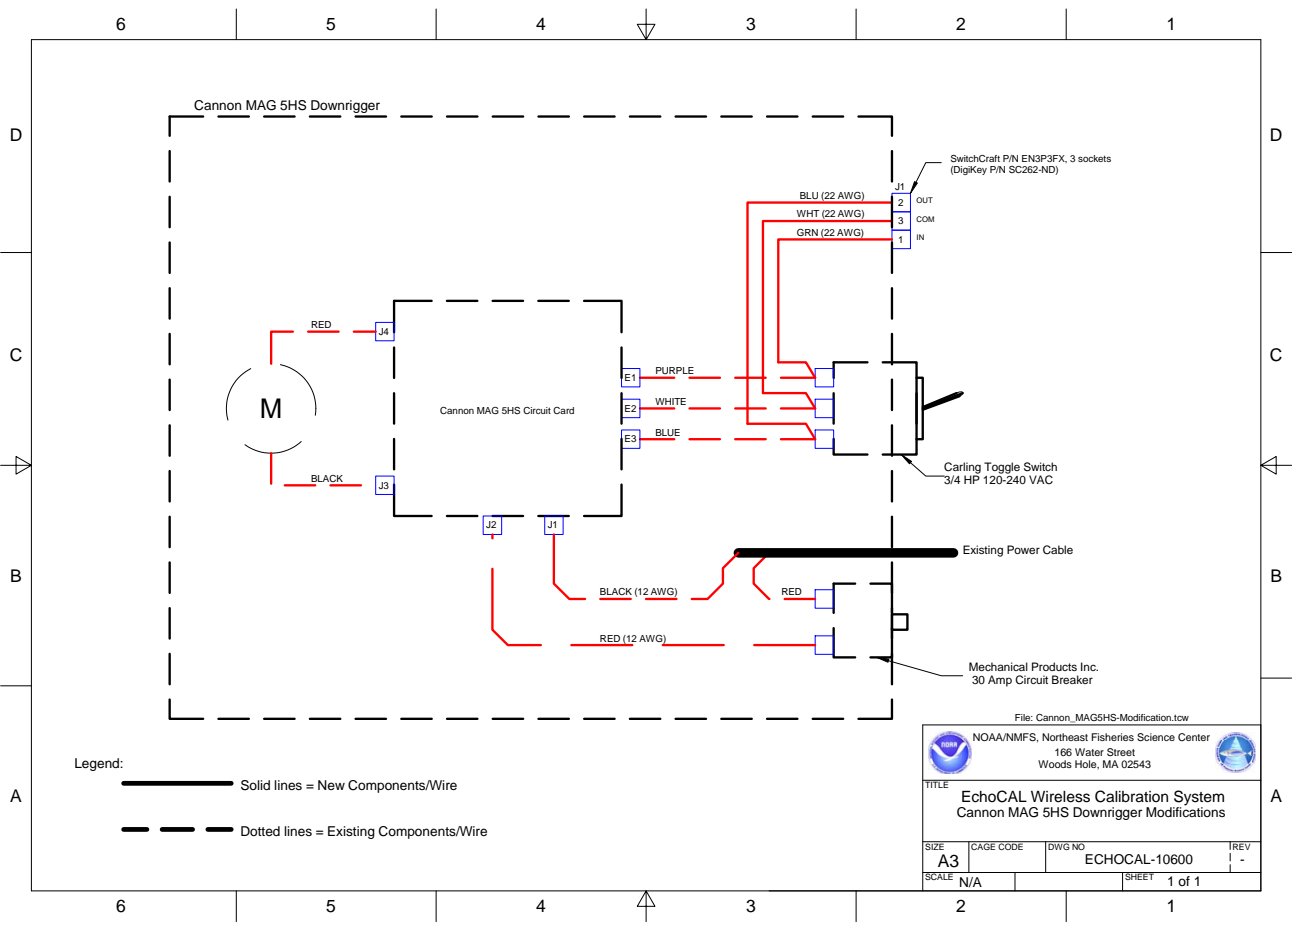
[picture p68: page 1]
SIZE; CAGE CODE; DWG NO; REV; ECHOCAL-10600; WHT (22 AWG); GRN (22 AWG); BLU (22 AWG); OUT; COM; SwitchCraft P/N EN3P3FX, 3 sockets (DigiKey P/N SC262-ND); PURPLE; WHITE; BLUE; RED; BLACK; BLACK (12 AWG); RED (12 AWG); Legend:

Cannon MAG 5HS Downrigger

Cannon MAG 5HS Circuit Card

Carling Toggle Switch
3/4 HP 120-240 VAC

Existing Power Cable

Mechanical Products Inc.
30 Amp Circuit Breaker

File: Cannon_MAG5HS-Modification.tcw

NOAA/NMFS, Northeast Fisheries Science Center

166 Water Street
Woods Hole, MA 02543

Solid lines = New Components/Wire

TITLE
EchoCAL Wireless Calibration System
Cannon MAG 5HS Downrigger Modifications

Dotted lines = Existing Components/Wire

SCALE N/A | SHEET

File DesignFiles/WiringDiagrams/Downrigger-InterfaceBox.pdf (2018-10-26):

D

D

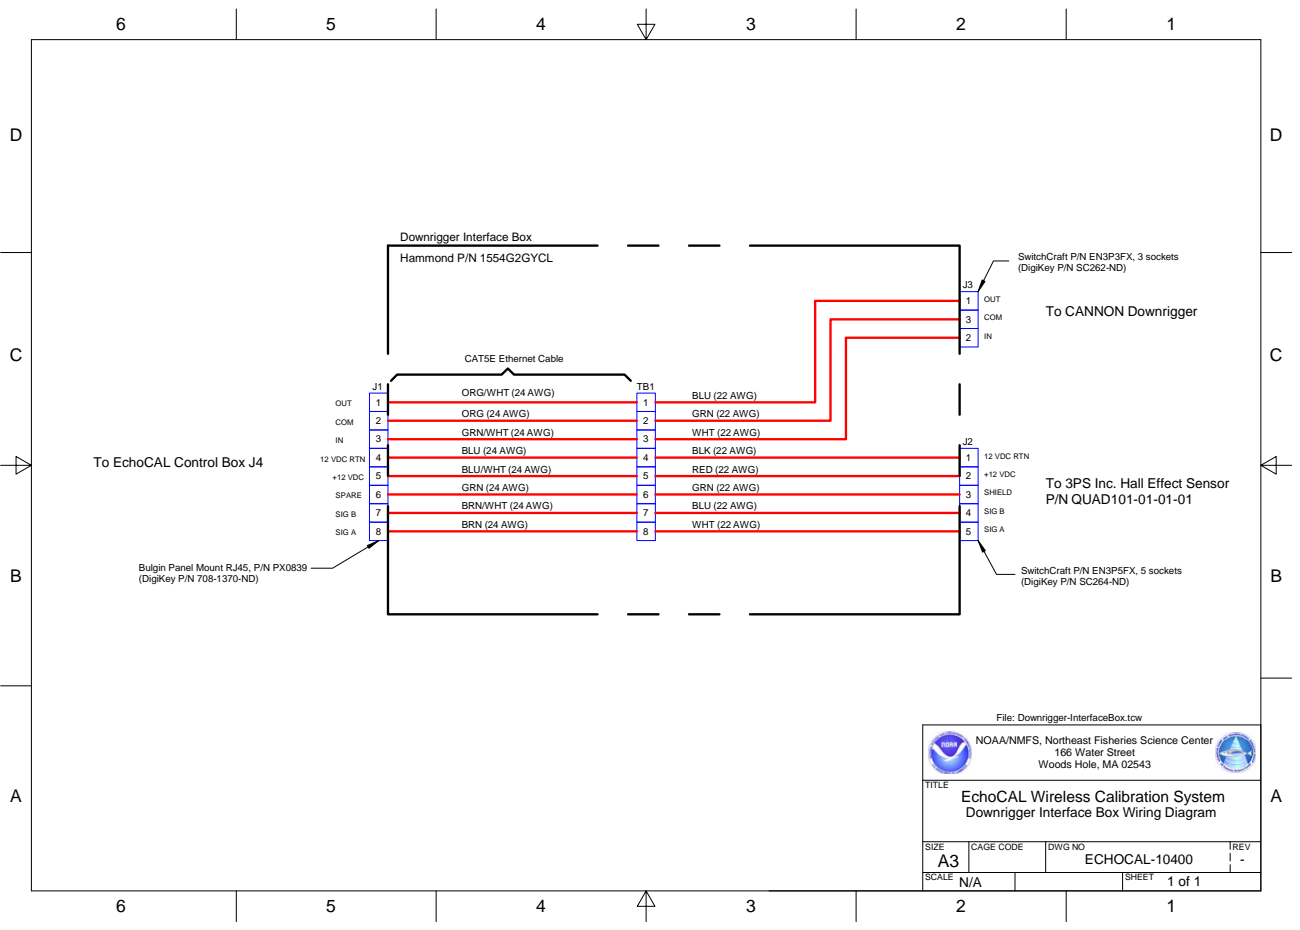
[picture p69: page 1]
SIZE; CAGE CODE; DWG NO; REV; ECHOCAL-10400; OUT; COM; 12 VDC RTN; +12 VDC; SPARE; SIG B; SIG A; CAT5E Ethernet Cable; BLK (22 AWG); RED (22 AWG); GRN (22 AWG); BLU (22 AWG); WHT (22 AWG); SHIELD; Hammond P/N 1554G2GYCL; SwitchCraft P/N EN3P3FX, 3 sockets; (DigiKey P/N SC262-ND); (DigiKey P/N 708-1370-ND); SwitchCraft P/N EN3P5FX, 5 sockets (DigiKey P/N SC264-ND)

Downrigger Interface Box

To CANNON Downrigger

ORG/WHT (24 AWG)

ORG (24 AWG)
GRN/WHT (24 AWG)
BLU (24 AWG)
BLU/WHT (24 AWG)
GRN (24 AWG)
BRN/WHT (24 AWG)
BRN (24 AWG)

To EchoCAL Control Box J4

To 3PS Inc. Hall Effect Sensor
P/N QUAD101-01-01-01

Bulgin Panel Mount RJ45, P/N PX0839

File: Downrigger-InterfaceBox.tcw
NOAA/NMFS, Northeast Fisheries Science Center

166 Water Street
Woods Hole, MA 02543

TITLE
EchoCAL Wireless Calibration System
Downrigger Interface Box Wiring Diagram

SCALE N/A | SHEET

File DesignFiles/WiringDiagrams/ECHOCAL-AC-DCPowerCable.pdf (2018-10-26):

D

D

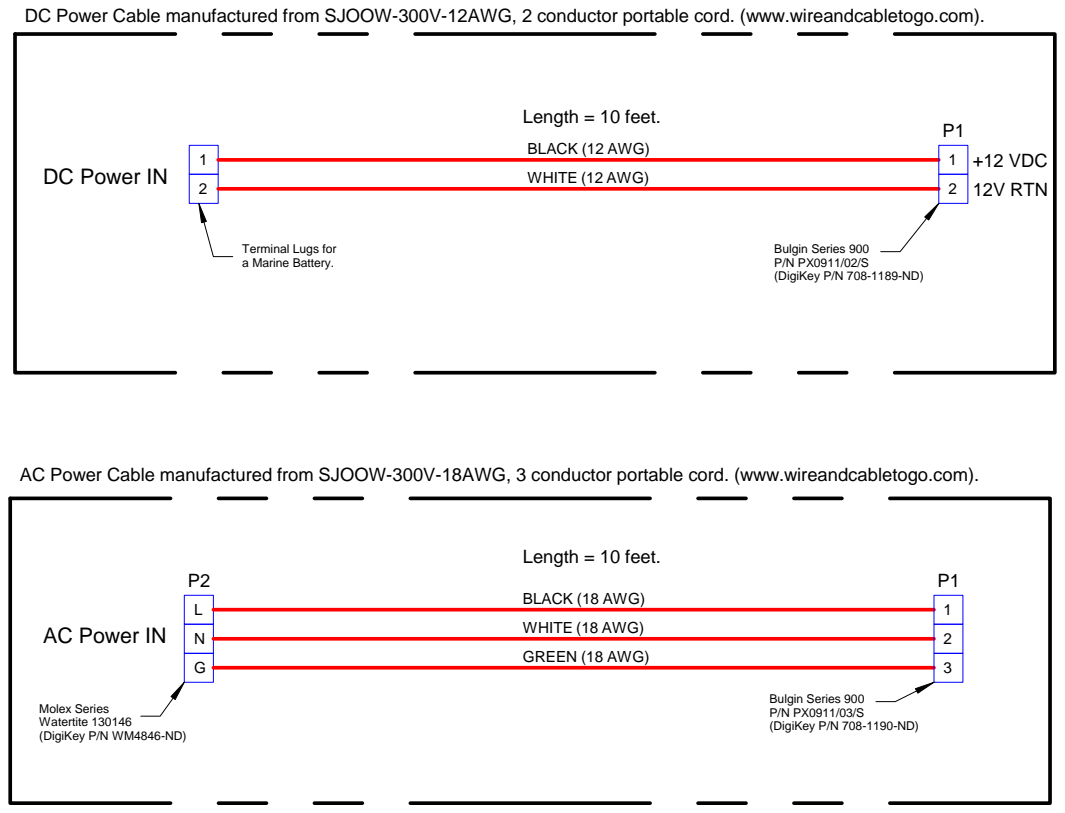
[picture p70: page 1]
SIZE; CAGE CODE; DWG NO; REV; ECHOCAL-10500; BLACK (18 AWG); WHITE (18 AWG); GREEN (18 AWG); Molex Series Watertite 130146 (DigiKey P/N WM4846-ND); Bulgin Series 900 P/N PX0911/03/S (DigiKey P/N 708-1190-ND); BLACK (12 AWG); WHITE (12 AWG); Bulgin Series 900 P/N PX0911/02/S (DigiKey P/N 708-1189-ND); Length = 10 feet.; +12 VDC 12V RTN

DC Power Cable manufactured from SJOOW-300V-12AWG, 2 conductor portable cord. (www.wireandcabletogo.com).

DC Power IN

Terminal Lugs for
a Marine Battery.

AC Power Cable manufactured from SJOOW-300V-18AWG, 3 conductor portable cord. (www.wireandcabletogo.com).

AC Power IN

NOAA/NMFS, Northeast Fisheries Science Center

166 Water Street
Woods Hole, MA 02543

TITLE
EchoCAL Wireless Calibration System
Power Cable Wiring Diagram

SCALE N/A | SHEET 1 of 1

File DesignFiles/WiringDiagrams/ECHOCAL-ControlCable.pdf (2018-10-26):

D

D

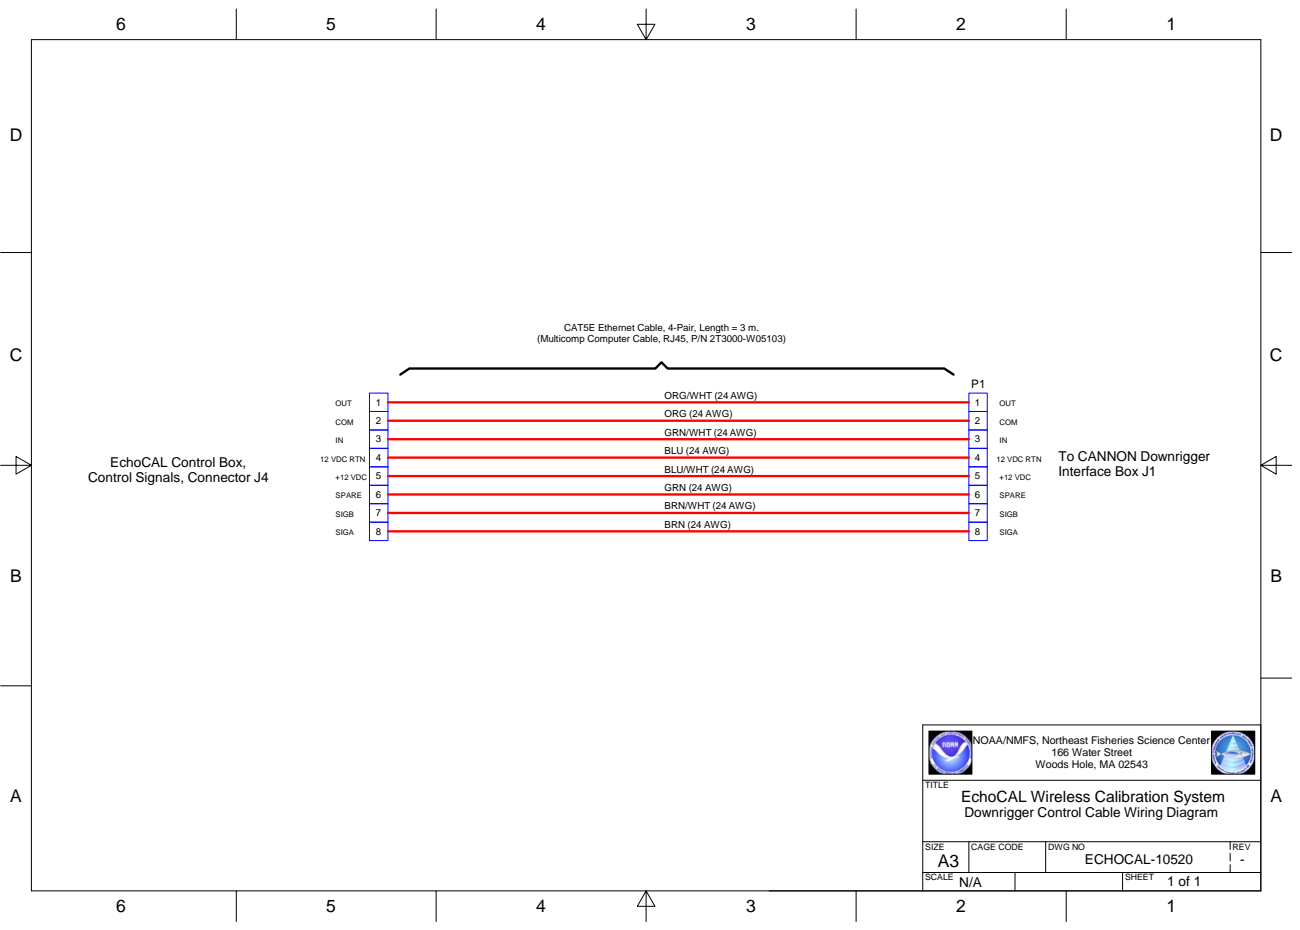
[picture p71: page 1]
SIZE; CAGE CODE; DWG NO; REV; ECHOCAL-10520; OUT; COM; 12 VDC RTN; +12 VDC; SPARE; SIGB; SIGA

CAT5E Ethernet Cable, 4-Pair, Length = 3 m.
(Multicomp Computer Cable, RJ45, P/N 2T3000-W05103)

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

EchoCAL Control Box,
Control Signals, Connector J4

To CANNON Downrigger
Interface Box J1

NOAA/NMFS, Northeast Fisheries Science Center

166 Water Street
Woods Hole, MA 02543

TITLE
EchoCAL Wireless Calibration System
Downrigger Control Cable Wiring Diagram

SCALE N/A | SHEET

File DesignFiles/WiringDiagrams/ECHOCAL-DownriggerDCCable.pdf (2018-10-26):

D

D

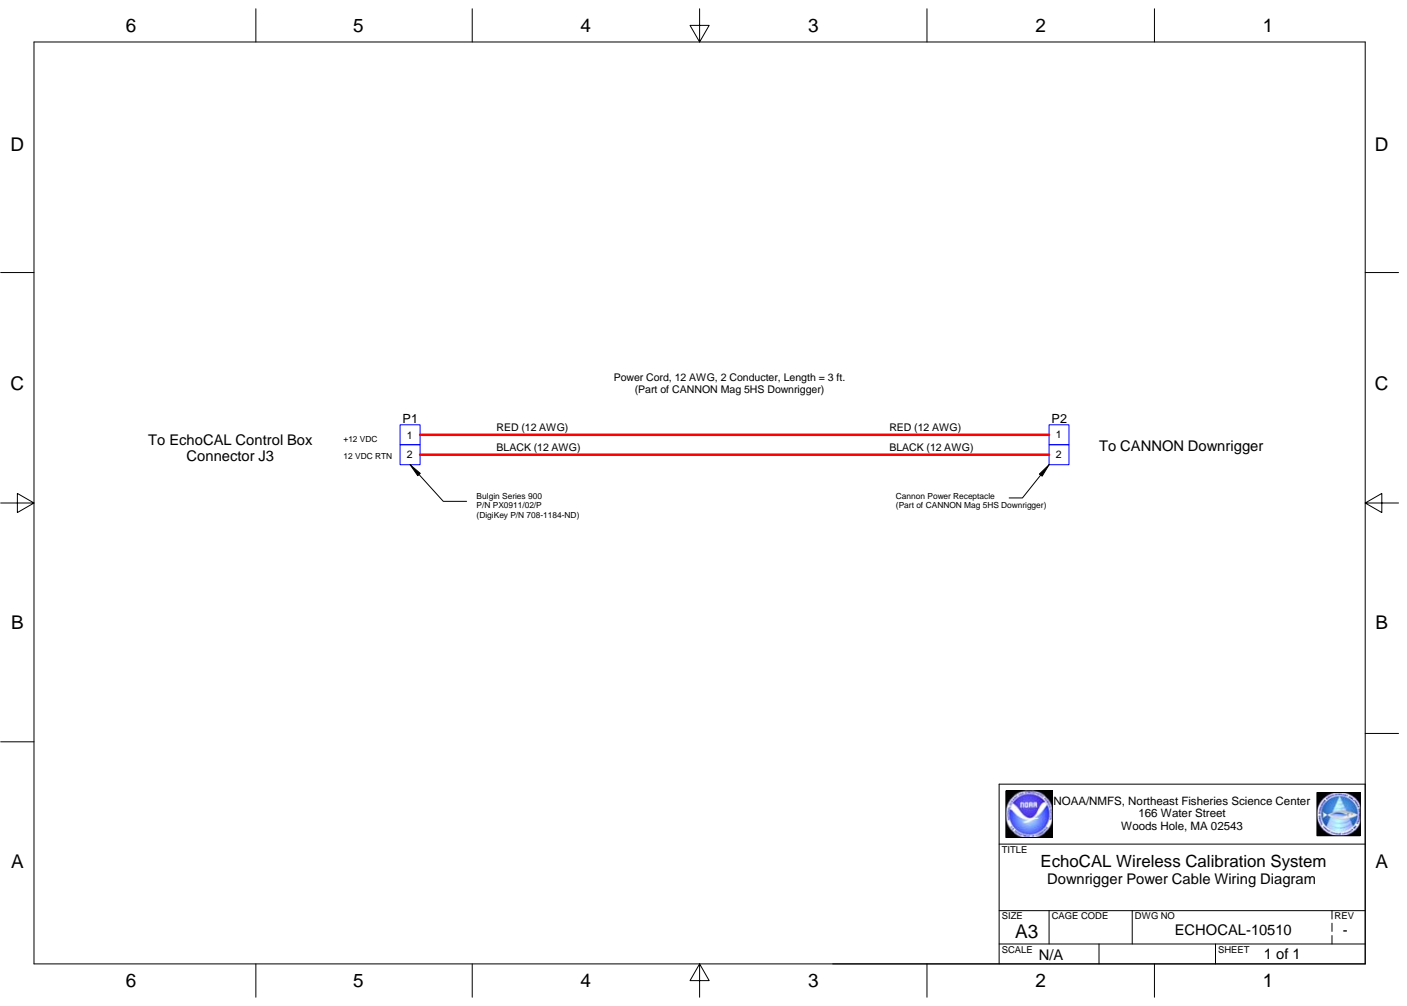
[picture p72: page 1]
SIZE; CAGE CODE; DWG NO; REV; ECHOCAL-10510; RED (12 AWG); BLACK (12 AWG); To CANNON Downrigger; Bulgin Series 900 P/N PX0911/02/P (DigiKey P/N 708-1184-ND); +12 VDC; 12 VDC RTN

Power Cord, 12 AWG, 2 Conducter, Length = 3 ft.
(Part of CANNON Mag 5HS Downrigger)

To EchoCAL Control Box
Connector J3

Cannon Power Receptacle

NOAA/NMFS, Northeast Fisheries Science Center

166 Water Street
Woods Hole, MA 02543

TITLE
EchoCAL Wireless Calibration System
Downrigger Power Cable Wiring Diagram

SCALE N/A | SHEET

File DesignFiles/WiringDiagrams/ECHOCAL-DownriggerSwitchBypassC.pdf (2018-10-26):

D

D

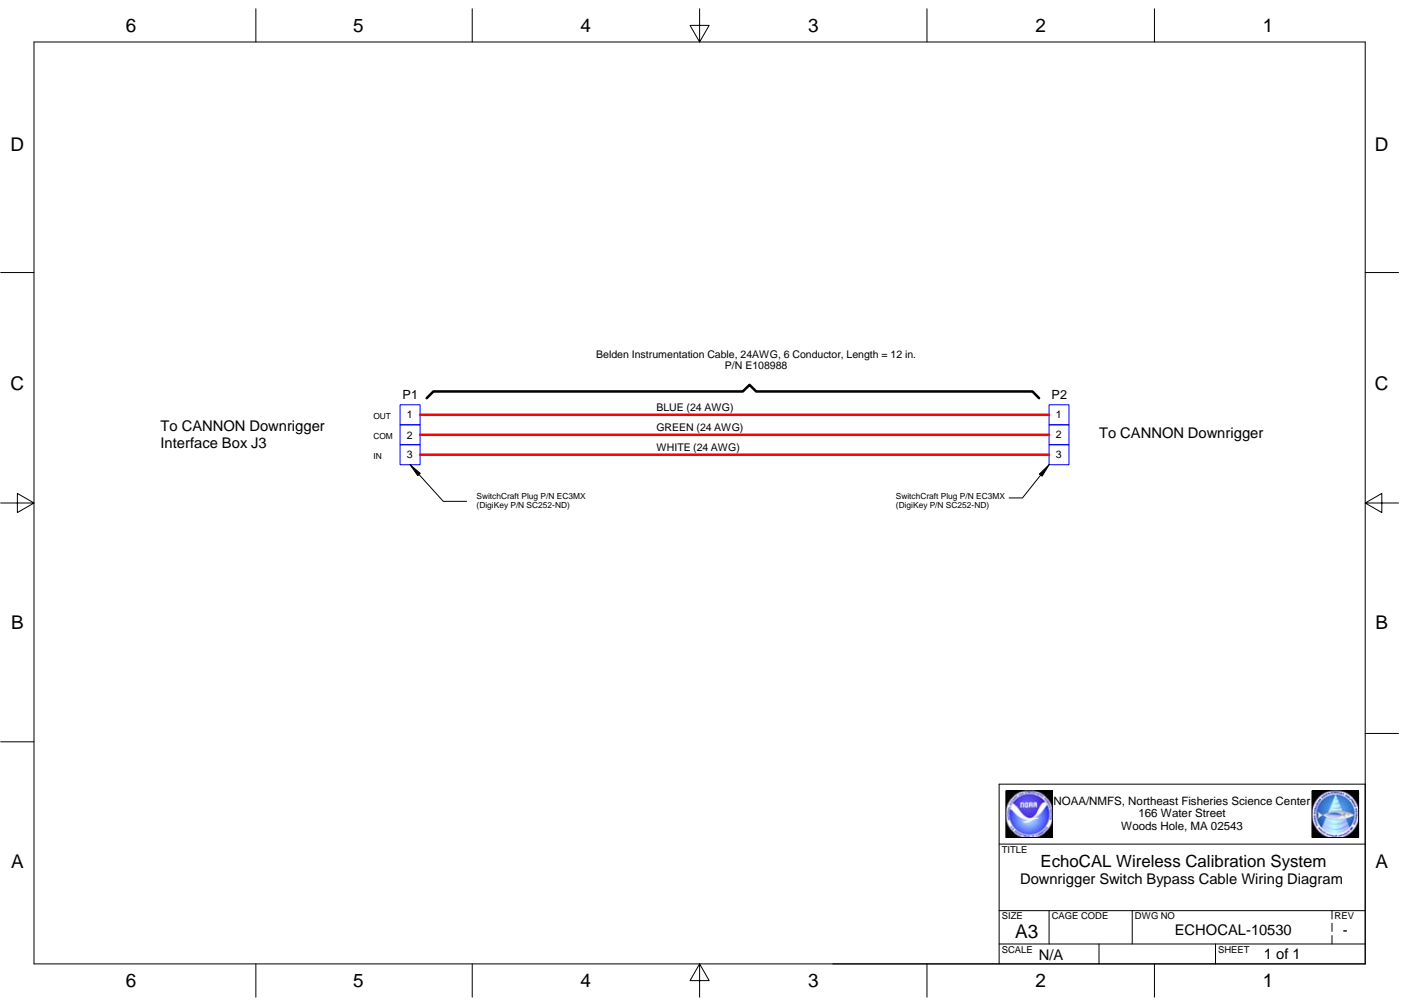
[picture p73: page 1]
SIZE; CAGE CODE; DWG NO; REV; ECHOCAL-10530; Interface Box J3; SwitchCraft Plug P/N EC3MX (DigiKey P/N SC252-ND); GREEN (24 AWG); WHITE (24 AWG); COM

Belden Instrumentation Cable, 24AWG, 6 Conductor, Length = 12 in.

BLUE (24 AWG) OUT

To CANNON Downrigger

NOAA/NMFS, Northeast Fisheries Science Center

166 Water Street
Woods Hole, MA 02543

TITLE
EchoCAL Wireless Calibration System
Downrigger Switch Bypass Cable Wiring Diagram

SCALE N/A | SHEET

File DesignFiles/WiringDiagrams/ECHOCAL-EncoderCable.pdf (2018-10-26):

D

D

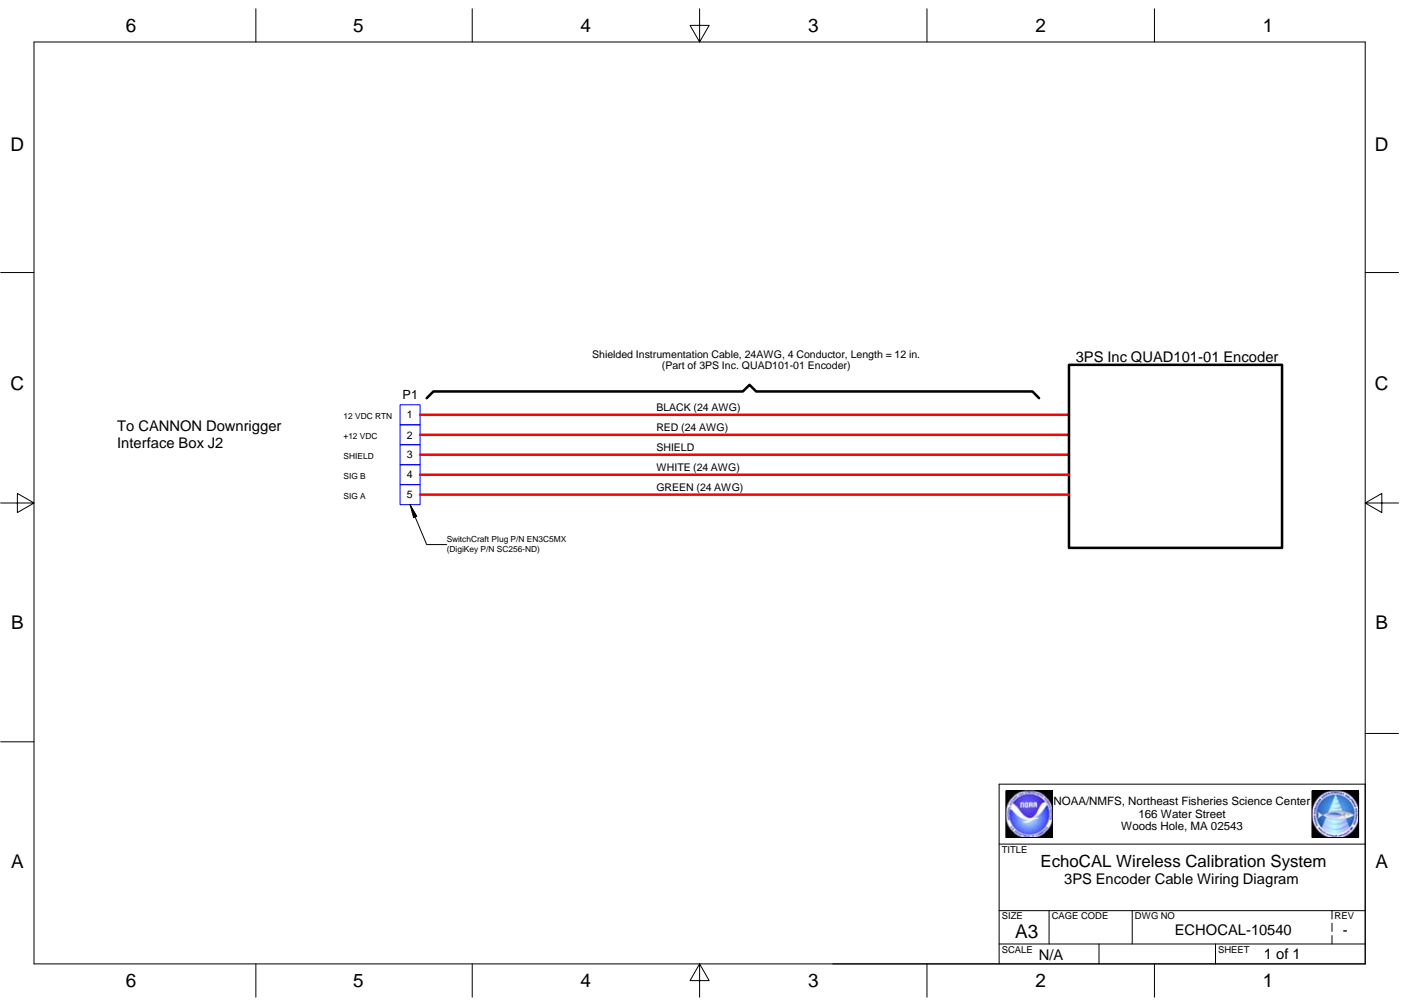
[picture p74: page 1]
SIZE; CAGE CODE; DWG NO; REV; ECHOCAL-10540; Interface Box J2; RED (24 AWG); SHIELD; 3PS Inc QUAD101-01 Encoder; SwitchCraft Plug P/N EN3C5MX (DigiKey P/N SC256-ND); BLACK (24 AWG); WHITE (24 AWG); GREEN (24 AWG); 12 VDC RTN; +12 VDC; SIG B; SIG A

Shielded Instrumentation Cable, 24AWG, 4 Conductor, Length = 12 in.

(Part of 3PS Inc. QUAD101-01 Encoder)

To CANNON Downrigger

NOAA/NMFS, Northeast Fisheries Science Center

166 Water Street
Woods Hole, MA 02543

TITLE
EchoCAL Wireless Calibration System
3PS Encoder Cable Wiring Diagram

SCALE N/A | SHEET

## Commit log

2018-10-26 Added Design Files and WGFAST info
    [BaseStation_BlockDiag.DXF, Cannon_MAG5HS_Modification.DXF, Downrigger-InterfaceBox.DXF, ECHOCAL-AC-DCPowerCable.DXF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]
2018-10-29 'Updated PCB drawing and added Readme.'
2018-10-29 Added License file to Circuit Card folder.
